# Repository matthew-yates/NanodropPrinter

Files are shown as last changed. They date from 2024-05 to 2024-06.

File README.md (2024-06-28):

# Nanodrop Printer

Syringe dispenser for accurately placing nanoliter scale liquid droplets on surfaces.

### XYZ motion hardware

The XYZ motion platform hardware is the [OpenBuilds C-Beam Machine](https://openbuildspartstore.com/openbuilds-c-beam-machine/):

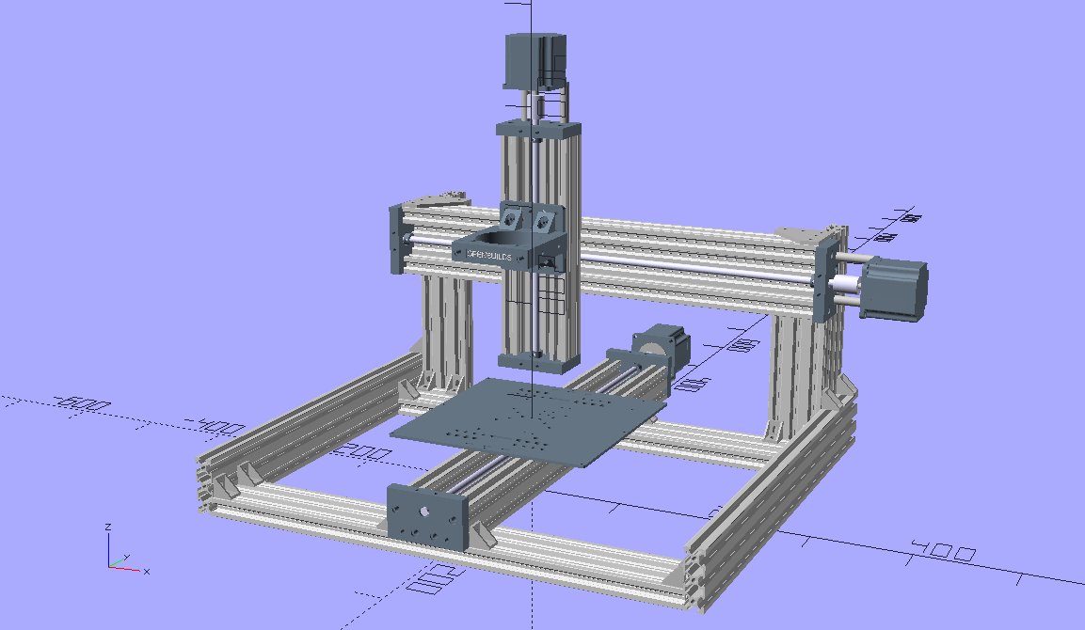
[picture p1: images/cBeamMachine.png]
C-Beam Machine


Identical [NEMA-23 stepper motors](https://openbuildspartstore.com/nema-23-stepper-motor/) with peak current of 2.8 A are used for the X, Y, and Z axes.

Motion is transmitted through [8 mm diameter lead screws](https://openbuildspartstore.com/8mm-metric-acme-lead-screw/) with 8 mm lead.

Moving parts are connected to the lead screws using [anti-backlash nuts](https://openbuildspartstore.com/anti-backlash-nut-block-for-8mm-metric-acme-lead-screw/).

Stepper motors have 200 full steps per revolution. The motors are operated with 1/16 microstepping, giving 2.5 microns of linear motion per microstep.

### Electronics

A [24 V Meanwell power supply](https://openbuildspartstore.com/24v-meanwell-power-supply-bundle/) is used to provide a maximum of 14.6 A current.

The [SKR mini E3 V3](https://github.com/bigtreetech/BIGTREETECH-SKR-mini-E3) is used for controlling stepper motors. The board uses [TMC2209 stepper drivers](https://www.analog.com/media/en/technical-documentation/data-sheets/TMC2209_datasheet_rev1.08.pdf) that are capable of driving motors up to 2.8 A.  This control board has four identical stepper drivers because it is designed for use in 3D printers.  Three of the stepper drivers are used to control X, Y, and Z motion.  The fourth is used to control a stepper motor on a syringe pump used for liquid deposition.

### Syringe pump

The syringe pump hardware is taken from a model [NE-300 pump](https://www.syringepump.com/NE-300.php). The syringe plunger motion is through a platform connected to a lead screw using an anti-backlash nut.  The lead screw has a lead of 1.27 mm per revolution. The lead screw is turned using a stepper motor connected with a belt and pulley system giving a motor:screw revolution ratio of 28:15.  The NE-300 stepper motor is a [high precision NEMA-17](https://www.moonsindustries.com/series/nema-17-high-precision-hybrid-stepper-motors-b020402) with 400 full steps per revolution.  Using 1/16 microstepping results in linear movement of the syringe plunger of 0.1 microns per microstep.

### Control software

[Marlin firmware](https://marlinfw.org/) is used for motion control. The motion commands are written in [G-code](https://en.wikipedia.org/wiki/G-code) format and sent to the microcontroller on the control board via serial communication with an attached computer.

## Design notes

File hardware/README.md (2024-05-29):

## Z-axis hardware

The Z-axis linear actuator of the Openbuilds C-beam machine has a spindle mount for attaching tools when used as a CNC machine.  This spindle mount is used to attached a syringe pump and BL-touch sensor.  The fully assembled Z-axis is illustrated below.

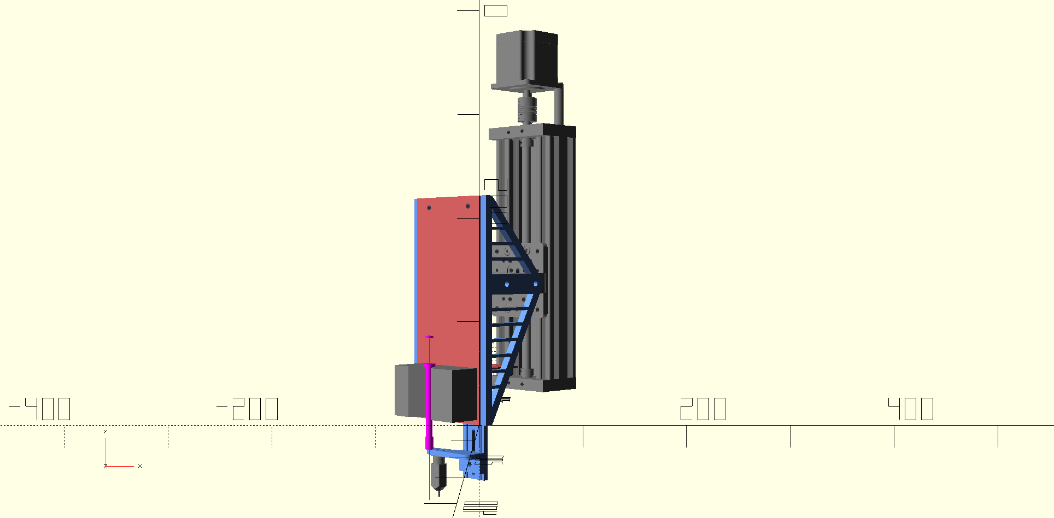
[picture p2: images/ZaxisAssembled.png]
Assembled BL-touch bracket


The image shows the approximate geometry of a mounted syringe and BL-touch sensor.  Folders in this hardware section of the repository include:

* [syringePump](https://github.com/matthew-yates/NanodropPrinter/tree/main/hardware/syringePump): Instructions with photographs for creating pump mounting plate from a model NE-300 syringe pump.
* [pumpBracket](https://github.com/matthew-yates/NanodropPrinter/tree/main/hardware/pumpBracket): Images, instructions, and OpenSCAD design files for 3D printed bracket for attaching syringe pump plate to spindle mount.
* [BLtouchMount](https://github.com/matthew-yates/NanodropPrinter/tree/main/hardware/BLtouchMount): Height adjustable mount for BL-touch sensor. Instructions and design files for 3D printing.

## Spring loaded plotter pen

In order to create fiducial markers for printing, the nanodroplet printer is used as a pen plotter. Fiducial markers are plotted on paper fixed to the glass platter printing surface. This approach ensures that the fiducial markers are aligned with the X and Y axes of the nanodroplet printer.

The widely available Pilot G2 Ultra Fine gel pen was selected for plotting. The refill cartridge was removed from the pen and used in a custom built holder that uses a spring to provide relatively constant force of the pen tip on paper. Design files and instructions for creating the spring loaded plotter pen are found in: [penPlotter](https://github.com/matthew-yates/NanodropPrinter/tree/main/hardware/penPlotter).

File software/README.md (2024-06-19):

# Instructions

## 1. Set up laptop for external instrument control

Although any operating system can be use in principle, all development and testing was done using the Debian Linux operating system.  The instructions here refer to that operating system and should be applicable to other Debian-based operating systems (Ubuntu, Mint, etc.).

### 1.1 Python related packages

After installing the Linux operating system, run the following command as root to install Python related packages:

```
apt install python3-full python3-numpy python3-scipy python3-sympy python3-matplotlib python3-opencv python3-pandas python3-serial python3-spyder jupyter-notebook
```

The above commands install a number of libraries used for scientific and numerical methods, serial communication, computer vision, the Spyder IDE for editing code, and Jupyter notebook client for running code interactively.

### 1.2 Serial communication

The user needs to be added to the "dialout" group in order to gain required permissions for sending commands to the printer. Run the following command as root to do this:

```
usermod -a -G dialout $USER
```

Where "$USER" is the name of the user to be added to the dialout group.

It is also recommended that PuTTY serial console be installed by running the following command as root:

```
apt install putty
```

PuTTY is not required, but can be useful in troubleshooting. To open a serial console to the instrument, use the speed (baudrate) setting of 115200.  The serial line is normally "/dev/ttyACM0". The serial line can be confirmed by running the command "dmesg" as root immediately after plugging the instrument into a USB port.  The PuTTY console can be left running in the background in order to display responses from the instrument.  For example, sending the G-code command "M119" will cause the instrument to respond with the current logic state of all endstop switches, which will be displayed on the PuTTY console.

### 1.3 PlatformIO

The [PlatformIO](https://docs.platformio.org/en/latest/core/index.html) command line interface is used for compiling the Marlin firmware. It is recommended that PlatformIO be installed on the laptop used for instrument control to facilitate making changes to firmware settings. First, install curl by running the following command as root:

```
apt install curl
```

Next, run the following two commands as a normal user:

```
curl -fsSL -o get-platformio.py https://raw.githubusercontent.com/platformio/platformio-core-installer/master/get-platformio.py
python3 get-platformio.py
```

This installation script will create a Python virtual environment in the user home directory in which platformio is installed.  The following two commands can be run as root to provide system-wide commands "platformio" and "pio" for any user to run:

```
ln -s /home/$USER/.platformio/penv/bin/platformio /usr/bin/platformio
ln -s /home/$USER/.platformio/penv/bin/pio /usr/bin/pio
```

Where "$USER" is the name of the user account used to run the platformio installation script.

## 2. Configure and install Marlin

A fork of the Marlin firmware used for the the SKR mini E3 V3.0 board is maintained in in a separate repository:

[https://github.com/matthew-yates/Marlin](https://github.com/matthew-yates/Marlin)

This repository can be downloaded as a zip archive.  After extracting the archive, run the following two commands as normal user from the directory containing the "platformio.ini" file:

```
platformio run --target clean -e STM32G0B1RE_btt_xfer
platformio run -e STM32G0B1RE_btt_xfer
```

The resulting compiled firmware will be found in the hidden subdirectory named ".pio/build/STM32G0B1RE_btt_xfer" found in the same directory that contains the "platformio.ini" file.

The compiled firmware is named "firmware.bin". Copy the compiled firmware to a microSD card formatted with the FAT32 filesystem. Insert the microSD card into the slot on the SKR mini E3 V3.0 board. The firmware will be installed from the microSD card automatically when the board is powered on.

The forked Marlin repository linked above contains the configuration files "Configuration.h" and "Configuration_adv.h" that can be edited if firmware changes are needed.

## 3. Motion calibration

### 3.1 X and Y axis lead screw calibration and XY plane skew

Refer to the README in the directory [leadCalibration](https://github.com/matthew-yates/NanodropPrinter/tree/main/software/leadCalibration). The calibration pattern provided is plotted using a pen plotter to calibrate linear travel per rotation of the lead screw and check for skew in the XY plane.

### 3.2 Z-axis syringe pump lead screw calibration

Movement on the Z-axis and syringe pump lead screws was measured using electronic calipers.  The microsteps per mm settings in the firmware were adjusted until the actual movement matched programmed movement.

### Camera calibration

A USB microscope is used to measure distances from images.  Accurate distances are needed for calculating XY coordinates for target printing locations.  Before the camera can be used for measurements, it must be calibrated by calculating the distance between two points on an image in pixels separated by a known distance in millimeters. A microscope calibration pattern is used for this purpose.

The Jupyter notebook file "cameraCalibration.ipynb" contains detailed annotated code for calibrating the camera. The following steps are involved:

1. The USB microscope is focused on the calibration pattern and an image of this pattern is saved using OpenCV. 
2. Two x,y pixel coordinates on the image then selected via mouse click. These points have a known distance in millimeters between them from the calibration pattern.
3. The distance between points in pixels is calculated.
4. Five repeated calibration measurements are taken, and the mean, maximum, minimum and standard deviation of the measured pixels per mm is reported.
5. The mean value is stored in a text file for future use as a conversion factor between pixels and millimeters.

The image below is an example image taken after clicking two calibration points.  In this case, a 5 mm calibration distance was selected and the microscope image was 1600x1200 pixels.

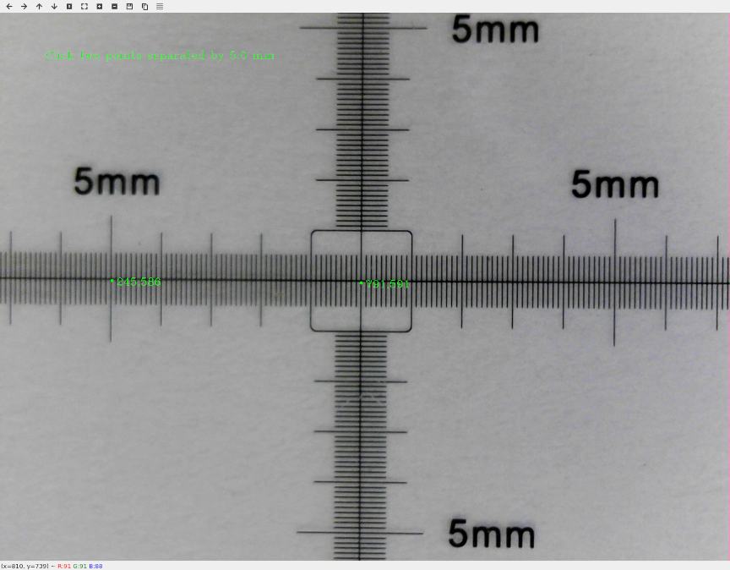
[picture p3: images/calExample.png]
example calibration image


### Fiducial marker

A fiducial marker is needed for alignment of the camera with the printer as well as accurately measuring locations of desired droplet deposition locations.  A variety of marker patterns are suitable for this purpose as long as there is a clear point that can be selected as the origin for x,y coordinates, as well as vertical and horizontal lines that define the directions of the printer axes.  An example marker is shown below.

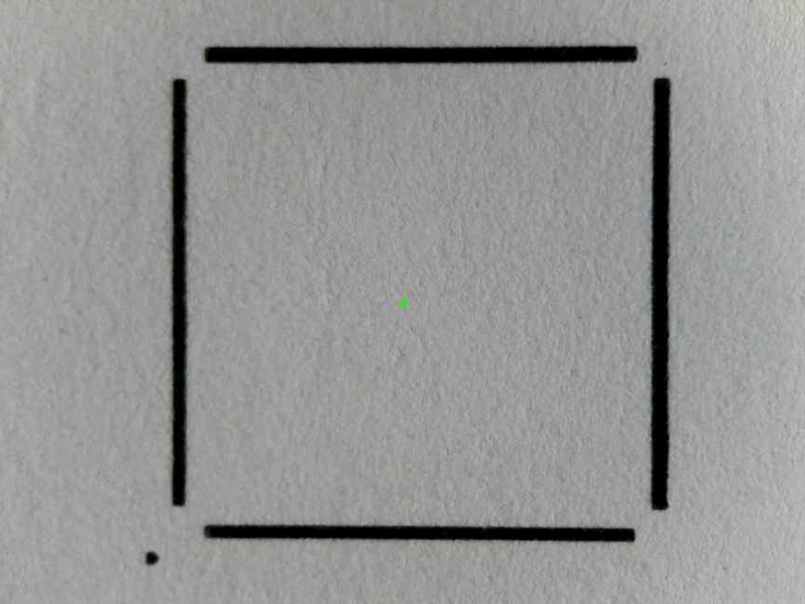
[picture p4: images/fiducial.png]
example fiducial marker


This marker has 4 lines, 8 mm x 0.2 mm each that are arranged to the edges of a 9 mm by 9 mm square shape.  The 9x9 mm^2 box defines an area in which small objects may be placed for selecting and measuring printing locations.  There is a small circle on the lower left that serves to mark the origin.  The above image is in scalable vector graphics format in the file "alignPattern.svg".

### Printer alignment with fiducial marker

The vertical and horizontal lines of the fiducial marker must be aligned with the y-axis and x-axis direntions of movement of the printer nozzle. The easiest way to achieve this is by using the printer itself as a plotter to create the fiducial marker. The syringe pump has a spring loaded clamp for holding a syringe. Instead of the syringe, clamp a fineliner marker or ultrafine technical pen.  Next, use the G-code file "alignMarker.gcode" to send motion commands needed to print the above pattern.  Before running the G-code commands, the marker should be placed in a starting position 1 mm above the target location of the origin dot. The print head is returned to this position after plotting the pattern.

### Camera alignment with the fiducial marker

Alignment of the camera image with the directions of the fiducial marker plotted by the printer is achieved by manually rotating the camera.  After it is aligned, the camera is clamped into position. To facilitate alignment, the Jupyter notebook "cameraAlignment.ipynb" can be used. The Python+OpenCV script places vertical and horizontal lines on the camera video feed. An example of camera alignment is shown in the image below.

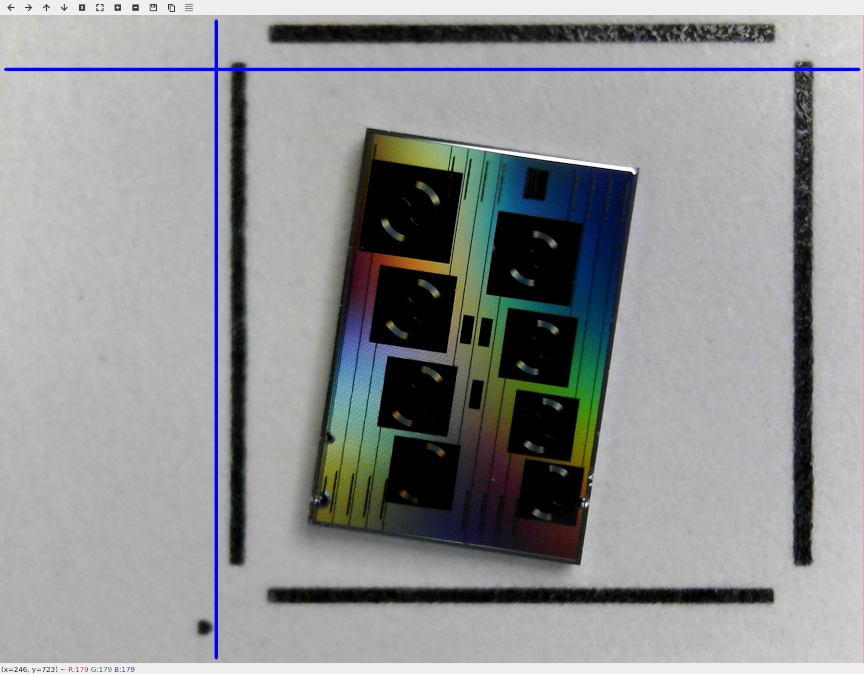
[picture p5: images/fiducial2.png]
example camera alignment


In this image, the blue lines are parallel to the fiducial marker lines. There is also a small silicon-based photonic chip in this image that is the target object for subsequent printing.

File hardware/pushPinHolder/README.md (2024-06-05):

## Push pin holder

A needle point push pin was used for testing accuracy of motion. When the tip of the pin is pressed into a plastic printing surface, it leaves a mark that can be used for measuring location in XY coordinates. For these motion accuracy tests, a simple holder was designed, as shown below.

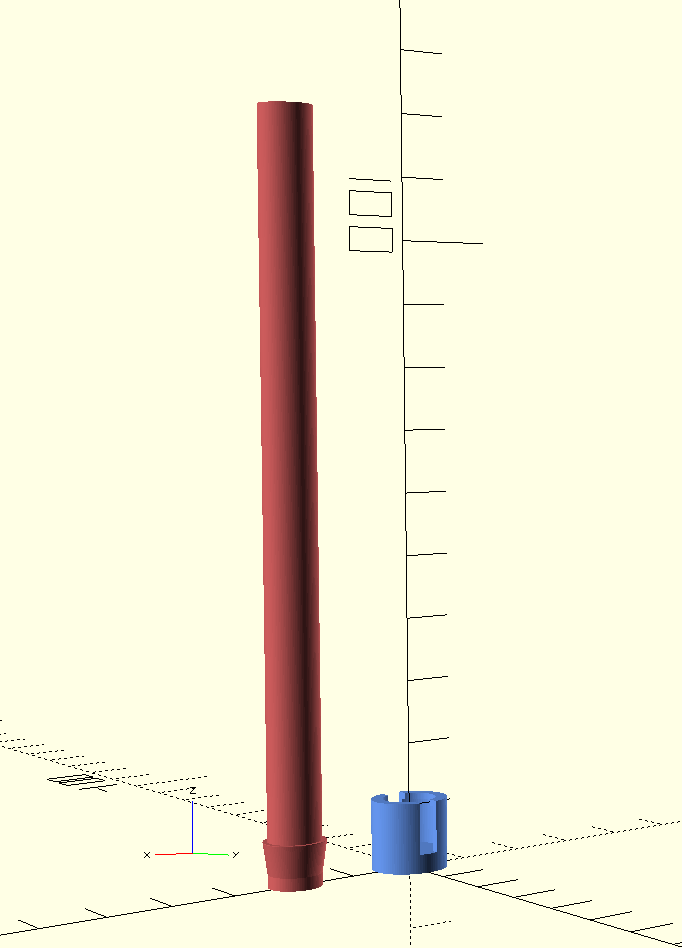
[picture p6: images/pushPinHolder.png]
push pin holder


It consists of a main body (shown in red) that has an annular ridge on the outside for attaching the cap (shown in blue). Before attaching the cap, the needle point pin is inserted through a small cylindrical opening. The fully assembled part is shown below with the needle illustrated in magenta.

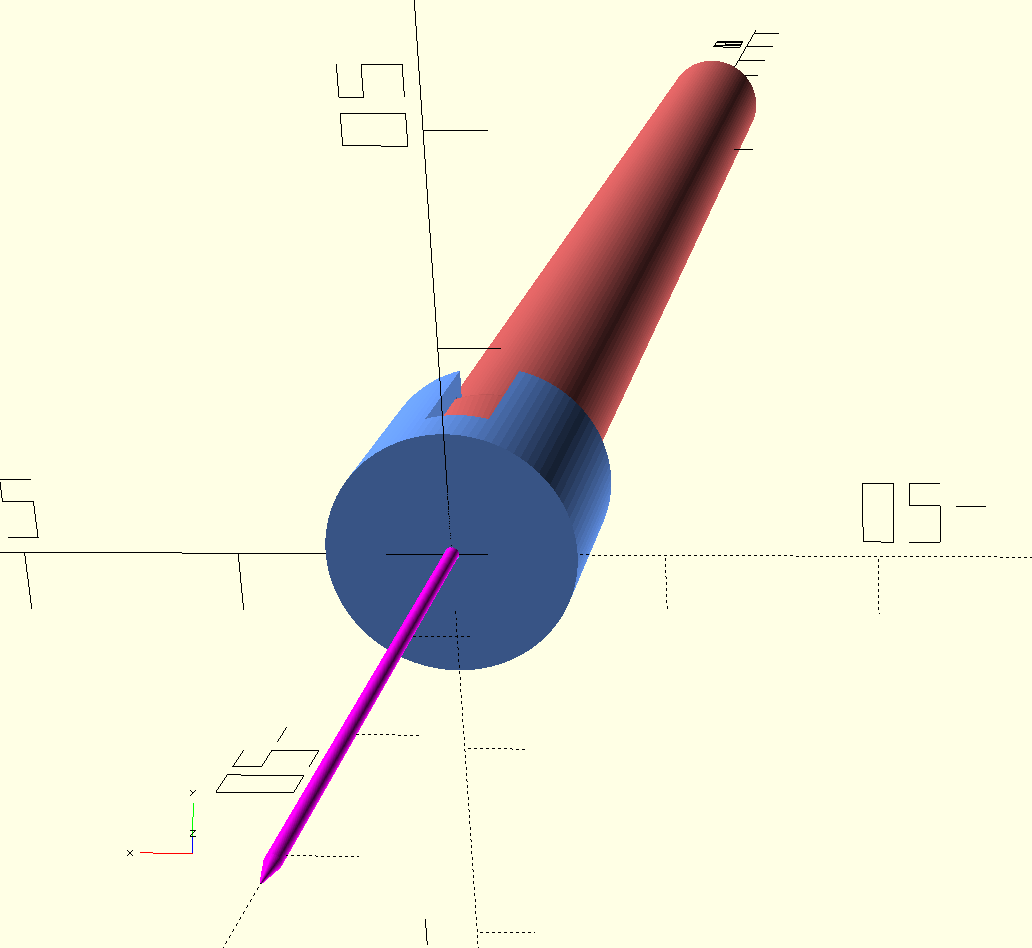
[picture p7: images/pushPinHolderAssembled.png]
assembled print bed with glass


The outer diameter of the main body of the holder is approximately the same as that of a Hamilton 25 microliter syringe model 80222. When the push pin holder is clamped into the syringe pump, the sharp point is therefore located at the approximately the same location as the center of a needle attached to the 25 microliter syringe.

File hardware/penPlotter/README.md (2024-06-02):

## Spring loaded pen

In order to ensure that fiducial markers are aligned with the X and Y axes of the nanodroplet printer, the printer itself was used as a pen plotter to draw lines. A variety of commercially available pens were tested for this purpose. The goal was to create very fine lines that are uniform in width. The widely available [Pilot G2 Ultra Fine](https://pilotpen.us/Product?0=40&1=29&cid=260) gel pen was selected. The manufacturer claims a line width of 380 microns. Testing showed the pen achieves relatively uniform line widths at or below 380 microns in width.  An example microscope image is show below of a hand drawn line on standard office copy paper. The microscope calibration ruler in the image measures in 100 micron increments. The image shows the pen produces a line ~300 microns in width. 

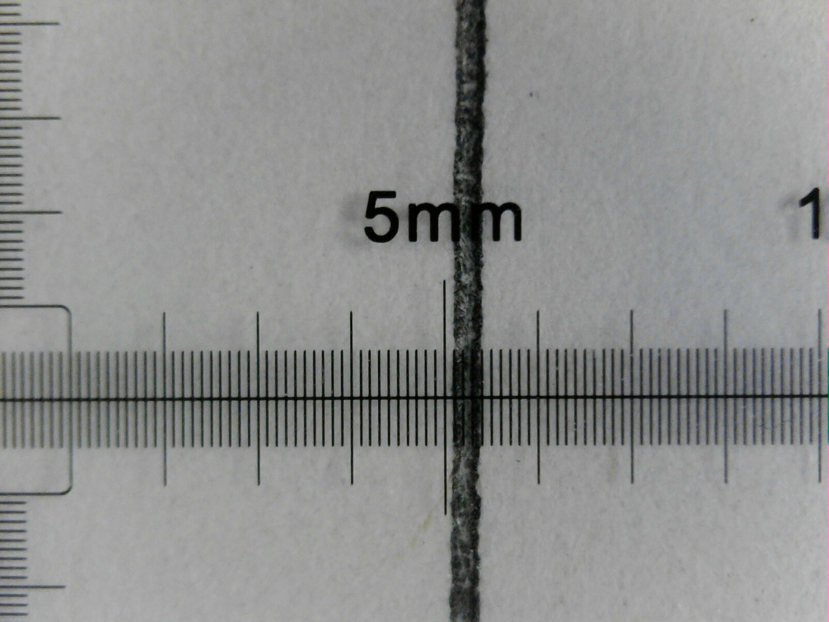
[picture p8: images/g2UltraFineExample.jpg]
pen line with microscope scale


The nanodroplet printer does not have an easy mechanism to control the force of contact of the pen in the Z-axis direction. To overcome this, a holder was developed that allows the pen tip a few millimeters of travel in the Z-axis direction. A spring is used to apply relatively constant force between the pen tip and plotting surface after contact is made.

### Fabrication and assembly

A 115.5 mm length piece is cut from [aluminum tubing](https://www.homedepot.com/p/Everbilt-36-in-x-1-2-in-x-1-16-in-Aluminum-Round-Tube-801247/204274002) having a nominal OD of 1/2 inch and wall thickness of 1/16 inch. A micrometer was used to measure the actual OD as 13 mm and ID as 9.7 mm. The aluminum tubing provides rigidity to minimize bending as the pen tip is dragged across the printing surface.

The Pilot G2 pen is disassembled to remove the refill and spring. The spring is re-used in the fabricated holder. The dimensions of the refill were measured by micrometer. A 3D model of the refill is provided in the file "ultraFineGelPen.scad".

Two parts must be 3D printed using the design file "ultraFineHolder.scad". The dimensions of these parts was determined by trial and error in order to have very right tolerances when printed using PETG filament. The library file "threadsDK.scad" created by Dan Kirshner is used for modeling threads for screwing the two parts together. The image of the 3D modeled parts is shown below.

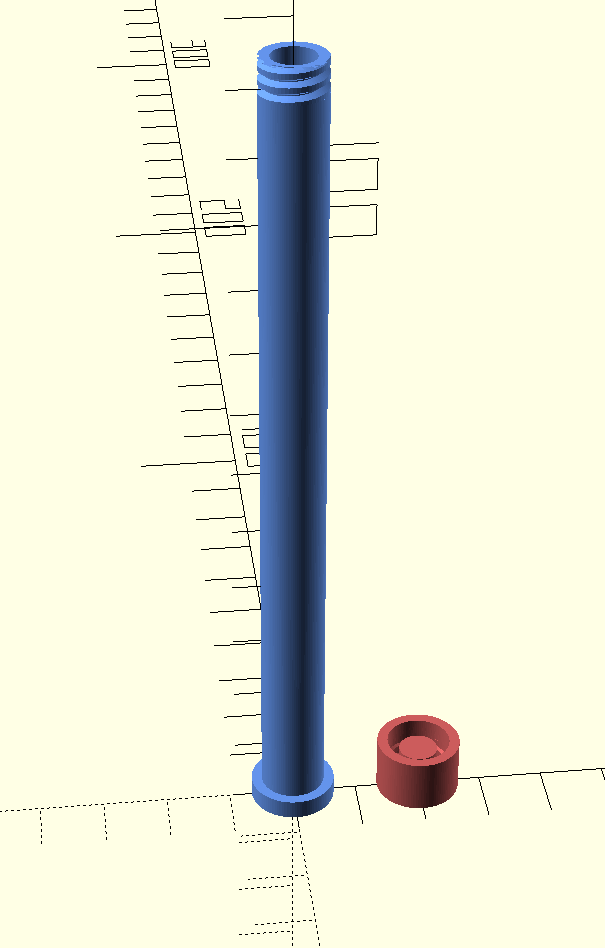
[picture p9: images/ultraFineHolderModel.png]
model used for 3D printed parts


After printing these parts, the long part shown in blue is slid inside the 115.5 mm long aluminum tube. The gel pen refill is inserted so that the pen tip extends out the hole at the base. The spring is inserted after the pen refill. The smaller part shown in red is screwed onto the top to compress the spring. An image of the final assembled part is shown below.

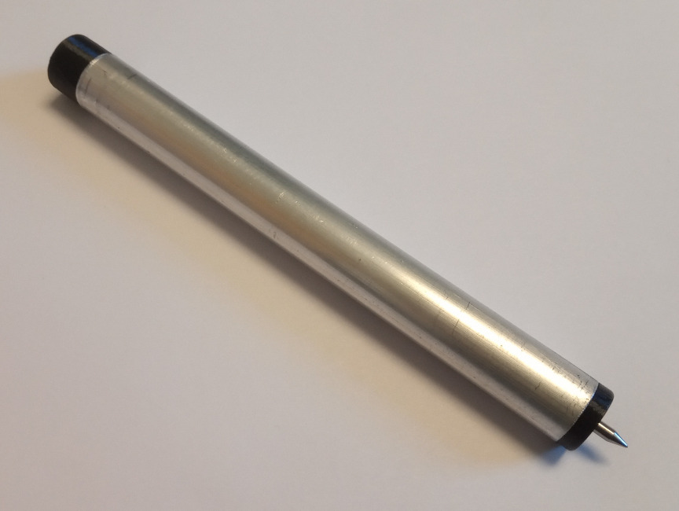
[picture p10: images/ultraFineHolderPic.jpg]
assembled spring loaded plotter pen

 
The plotter pen is attached to the syringe pump using the spring loaded clip normally used for syringes. A metal C-clamp is then used to firmly hold the plotter pen is place as it is dragged laterally across the printing surface during plotting. An adapter part was designed in "penClampClip.sscad", a model of which is shown below.

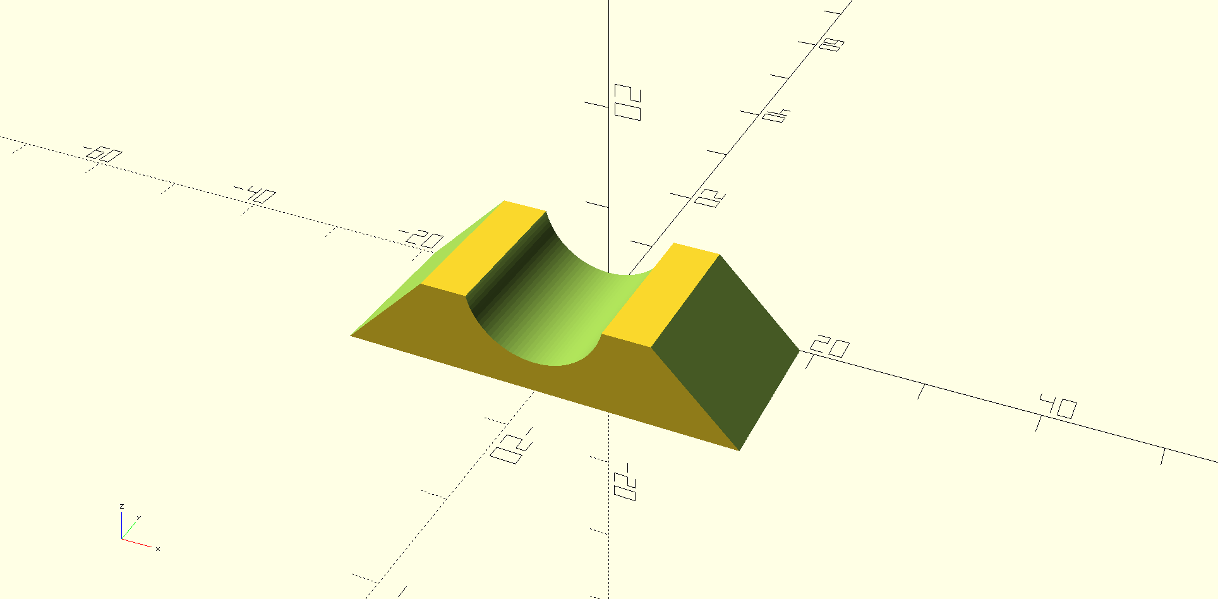
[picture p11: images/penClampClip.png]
plotter pen c-clamp adapter


This C-clamp adapter is placed on top of the plotter pen to prove a flat surface for attaching the clamp. An image of the fully assembled device with the plotter pen held by a small C-clamp is shown below.

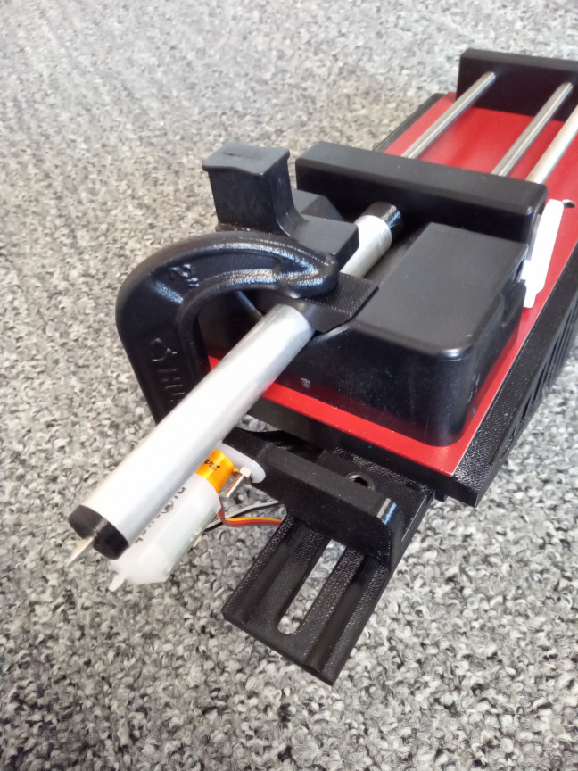
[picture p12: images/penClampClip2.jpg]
fully assembled plotter pen


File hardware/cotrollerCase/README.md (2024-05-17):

## Case for motion controller

Currently using the BigTreeTech SKR mini E3 V3.0 board with Marlin firmware to control movement.  The case for this control board and an LCD screen is decribed in a separate repository:

[https://github.com/matthew-yates/BTTskrE3v3_case](https://github.com/matthew-yates/BTTskrE3v3_case)

Possibly switching to a different control board in the future, which will require designing a new case.

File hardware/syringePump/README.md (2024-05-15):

## Syringe pump

The hardware for liquid dispensing is taken from a model [NE-330](https://www.syringepump.com/NE-300.php) syringe pump, illustrated below.

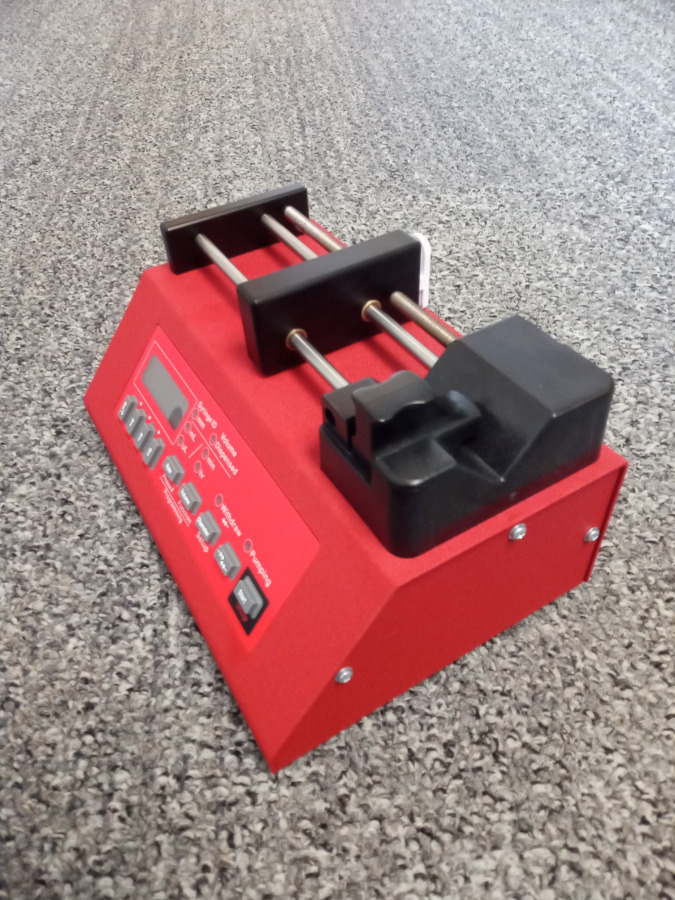
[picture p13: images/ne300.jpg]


The the pump is first fully disassembled. After removing all of the parts mounted to the top cover, it is cut along the approximate lines illustrated in green in the image below.

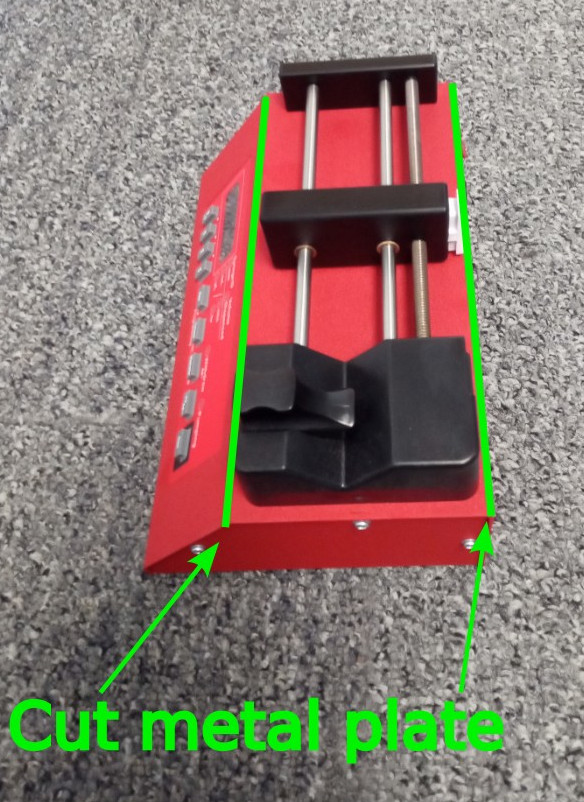
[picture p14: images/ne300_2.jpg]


The portion of the top cover cut out is a rectangle having dimensions of 92 mm by 222 mm. After cutting off the two screw tabs, the bottom side is flat.  An image of the cut out portion is shown below.  

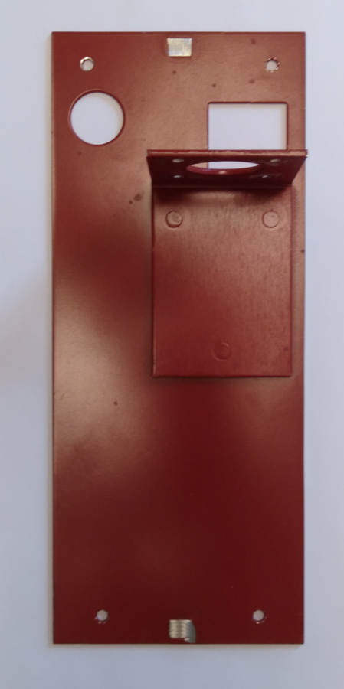
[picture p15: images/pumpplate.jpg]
pump plate image


The two screw tabs used to attach the top cover to the bottom cover were cut off.  This plate has a NEMA-17 stepper motor mount, large rectangular opening for the stepper belt/pulley connection between the stepper motor and the lead screw, and a large circular opening for the spring loaded syringe holder.  In addition, there are five small screw holes in the plate from the manufacturer.  These screw holes are used to attach parts to the plate using #6 coarse grain machine screws.  The NEMA-17 stepper is mounted to the motor mount using four M3 screws.

Not shown on the above image of the plate are two additional screw holes required for attaching the plate to the spindle mount on the XYZ positioning system.  These holes must allow M5 screws to pass through (~5.5 mm in diameter).  They are locate 9.2 mm from each long edge of the rectangle.  A 3D model of the plate was created in OpenSCAD that has precise dimensions of this plate.  The OpenSCAD code in this repository has the precise locations of all screw holes.  A rendering of this model is shown below.

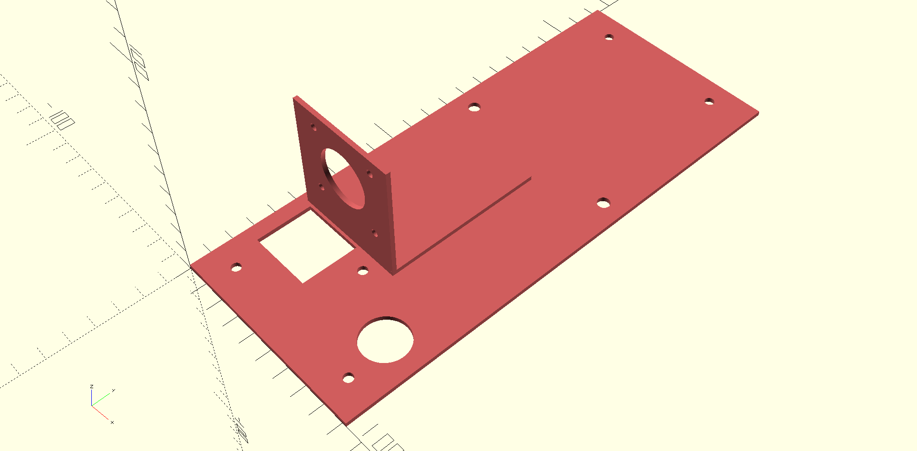
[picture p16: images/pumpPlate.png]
pump plate 3D model


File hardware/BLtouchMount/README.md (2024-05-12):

## Adjustable BL-touch mounting bracket

This is a height adjustable mount for a [BL-Touch sensor](https://www.antclabs.com/bltouch).  The sensor allows the location of the printing surface to be detected.  This mounting bracket is placed on the back side of the syringe pump.  The adjustable height of the bracket allows it to be used with syringes of varying length.  The image below shows the two parts of the bracket colored in blue and red.

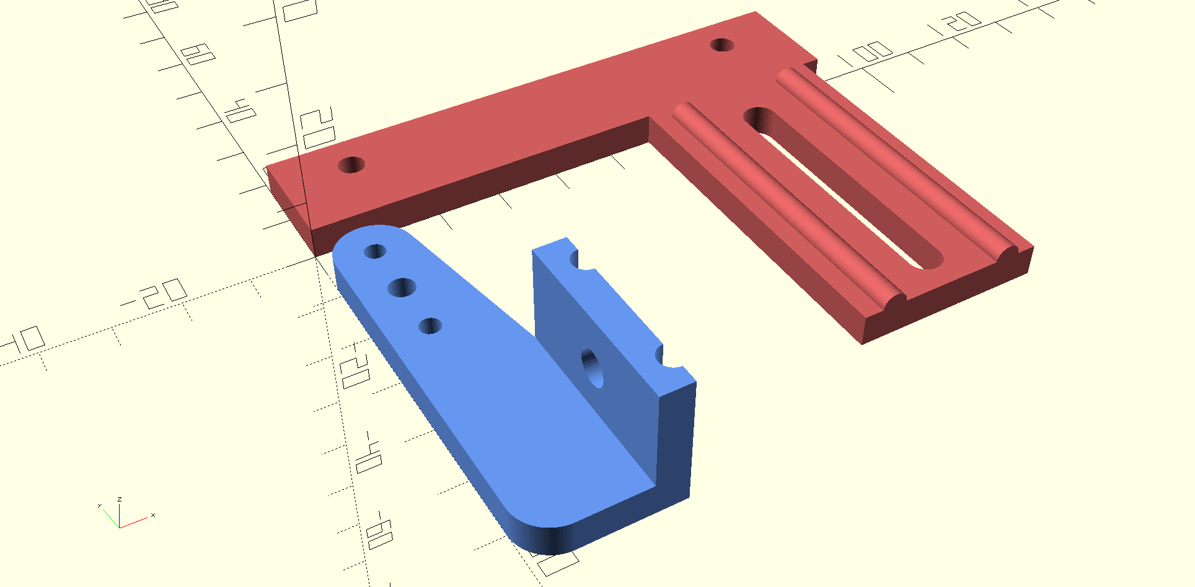
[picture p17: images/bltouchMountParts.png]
Bracket to mount BL-touch sensor


The next image below shows the two part bracket assembled with the BL-Touch sensor illustrated in gray.  The vertical slot in the bracket allows for height adjustment using an M5 size screw and nut.

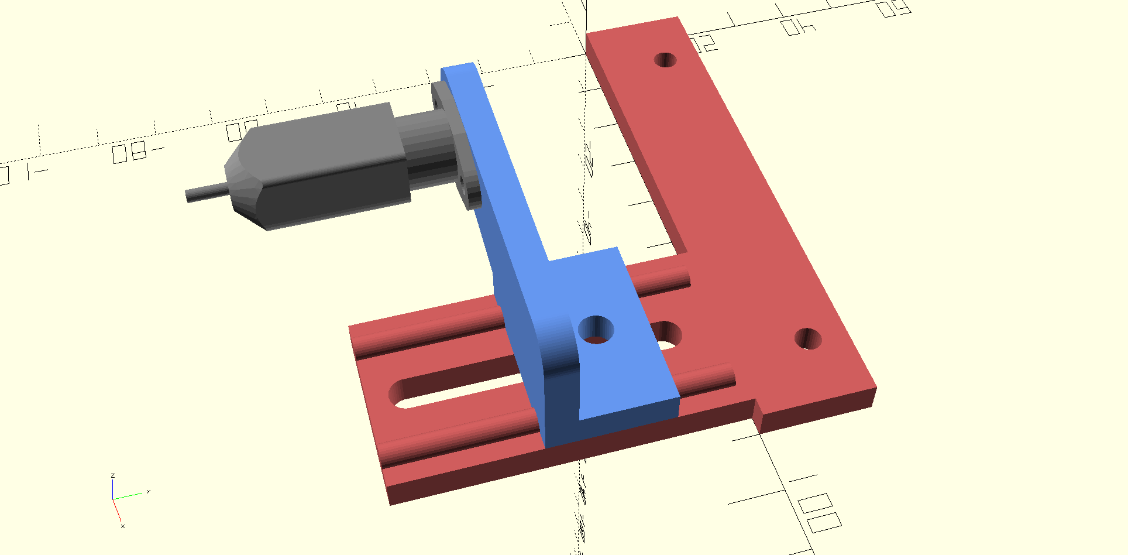
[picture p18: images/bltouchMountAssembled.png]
Assembled BL-touch bracket


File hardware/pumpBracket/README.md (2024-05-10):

## Syringe pump mounting bracket

The NE-300 syringe pump hardware is mounted to the spindle mount on the Openbuilds C-beam machine. The image below shows the rendering of the mounting bracket in blue.  The part of the spindle mount is shown in gray. The syringe pump parts are shown in red.  The bracket is secured to the spindle mount using M5 screws on the existing tapped holes. 

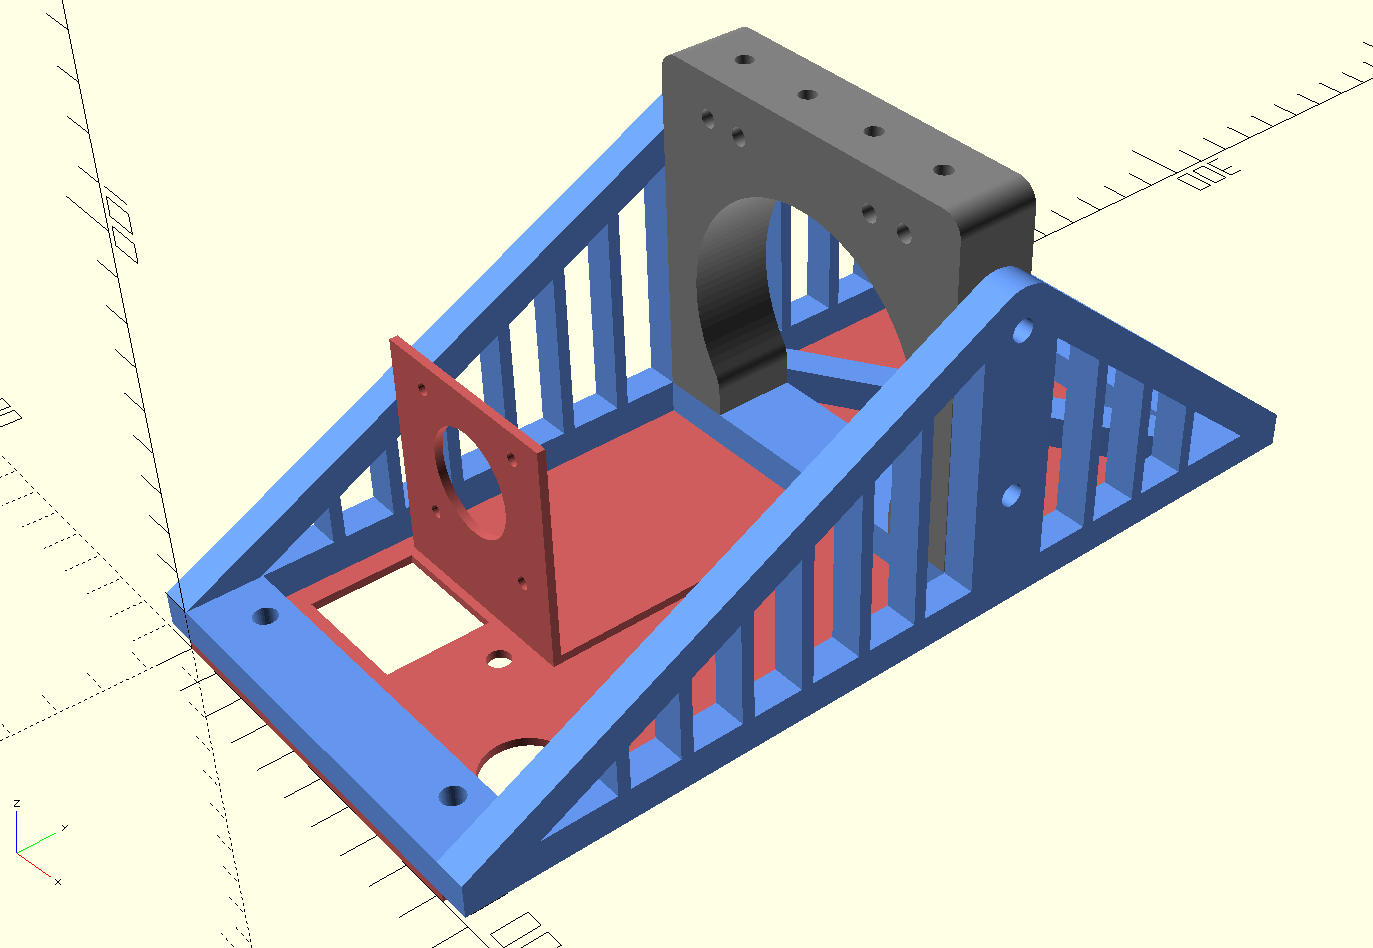
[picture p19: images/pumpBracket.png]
Bracket to mount syringe pump


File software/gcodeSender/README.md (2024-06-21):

## Sending G-code motion commands via serial communication

The Jupyter notebook "gcodeSender.ipynb" is used to send an arbitrary sequence of G-code motion commands from an attached laptop through USB serial connection to the printer.  The motion commands are read from a comma separated variable file that has absolute positions of X, Y, Z, and E (syringe pump/extruder) in individual columns.  Two example csv files are provided that can be used with a pen plotter.  The file "circle.csv" plots a single circle having a radius of 30 mm.  The file "plotPoints.csv" produces 4 concentric rectangles used for linear lead screw travel calibration.

When sending commands via serial communication, the commands must be spaced apart in time in order to avoid overflowing the buffer on the printer controller.  When serial commands are sent too quickly, the buffer overflow will cause commands to be skipped. The Python script calculates the time required for each movement based on the maximum travel speed settings in firmware which are 5 mm/s for X, Y, and Z axes and 0.7 mm/s for the E axis (syringe pump plunger). Sleep times are added between motion commands to allow enough time for printer movement to complete before issuing the next motion command.

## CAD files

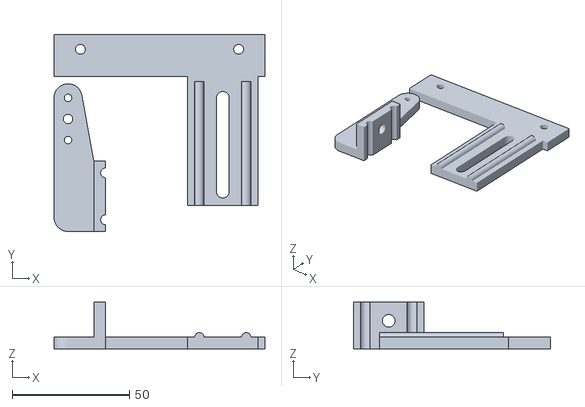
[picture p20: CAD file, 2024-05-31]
hardware/BLtouchMount/bltouchMountParts.stl
90.0 x 84.0 x 20.0

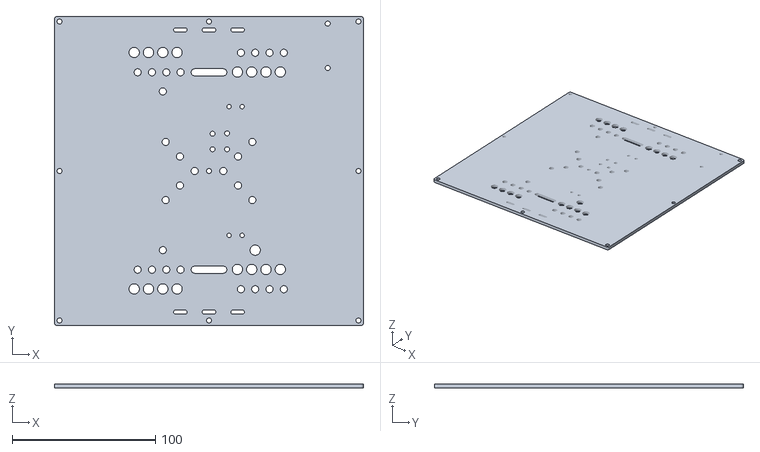
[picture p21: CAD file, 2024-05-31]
hardware/printBed/buildPlate.stl
216.0 x 216.0 x 3.00

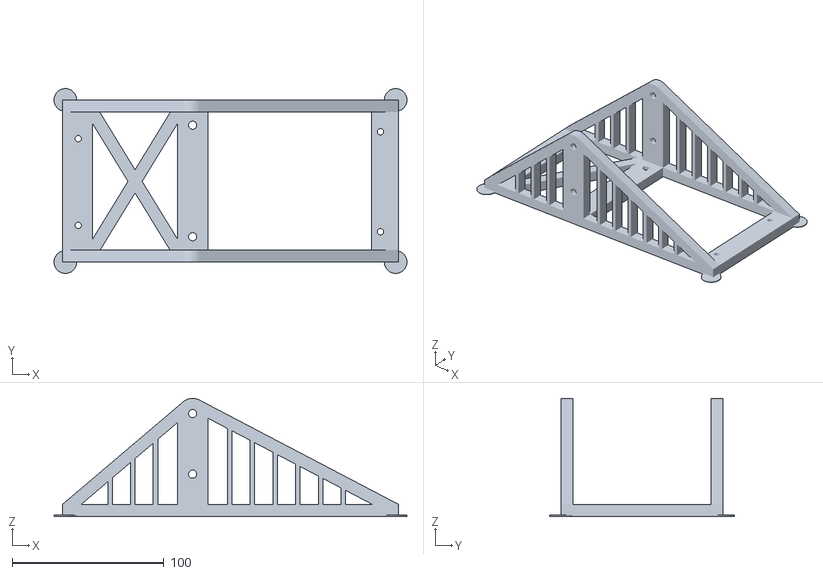
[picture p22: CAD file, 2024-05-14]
hardware/pumpBracket/pumpBracket.stl
233.0 x 122.0 x 78.0

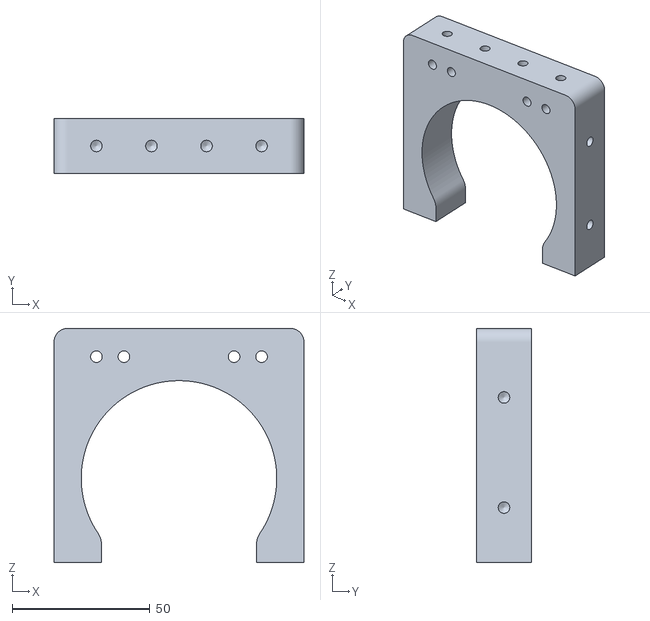
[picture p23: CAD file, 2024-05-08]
hardware/pumpBracket/spindlemount.stl
90.8 x 20.0 x 85.1

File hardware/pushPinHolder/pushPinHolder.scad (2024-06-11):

$fa = 1;
$fs = 0.4;
$fn=100;

color("cornflowerblue"){
difference(){
    cylinder(h=11.2,r=5.9);
    translate([0,0,3]) cylinder(h=11,r=4.9);
    translate([-1.5,-7.5,3]) cube([3,15,12]);
    translate([0,0,-1]) cylinder(h=5,r=0.5);
    translate([0,0,2]) cylinder(h=3,r=1.);
    }
difference(){
    translate([0,0,10.2]) cylinder(h=1,r=5.9);
    translate([0,0,3]) cylinder(h=11,r=4.2);
    translate([-1.5,-7.5,3]) cube([3,15,12]);
    }
}
        
translate([20,0,0])
color("indianred"){
difference(){
    union(){
        hull(){
            translate([0,0,2]) cylinder(h=0.1,r=4.1);
            translate([0,0,7]) cylinder(h=0.1,r=4.8);
            }
        cylinder(h=120,r=4.1);
        }
    translate([0,0,5]) cylinder(h=119,r=3.25);
    }
}

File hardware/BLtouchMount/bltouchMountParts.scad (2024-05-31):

$fa = 1.0;
$fs = 0.4;
translate([11,-60,5]) rotate([0,180,0])
// Vertical adjustment mount
color("cornflowerblue"){
    // bottom plate
    difference(){
        hull(){
            translate([5,0,0]) cylinder(h=5,r=6);
            translate([5,51,0]) cylinder(h=5,r=6);
            translate([-6,-6,0]) cube([5,30,5]);}
        // screw holes for top of BL touch
        translate([5,33,-1]) cylinder(h=7,r=1.6);
        translate([5,51,-1]) cylinder(h=7,r=1.6);
        // center hole on BL touch
        translate([5,42,-1]) cylinder(h=7,r=2);
        // slots for vertical adjustment
        translate([-11,-1,-1]) cylinder(h=27, r=2.1);
        translate([-11,19,-1]) cylinder(h=27, r=2.1);}
    // side plate
    difference(){
        translate([-11,-6,-15]) cube([5,30,20]);
        // M5 screw hole for height adjustment
        translate([-15,9,-7]) rotate([0,90,0]) cylinder(h=10,r=2.7);
        // slots for vertical adjustment
        translate([-11,-1,-16]) cylinder(h=27, r=2.1);
        translate([-11,19,-16]) cylinder(h=27, r=2.1);
}}
//Bracket to attach to pump
color("indianred"){
difference(){
    union(){
        cube([90,18,5]);
        translate([57,-55,0]) cube([30,55,5]);
        translate([62,-55,5]) rotate([-90,0,0]) cylinder(h=53,r=2);
        translate([82,-55,5]) rotate([-90,0,0]) cylinder(h=53,r=2);}
    // slot for vertical adjustment
    hull(){
    translate([72,-49,-1]) cylinder(h=7,r=2.7);
    translate([72,-9,-1]) cylinder(h=7,r=2.7);}
    // #6 screw holes for mounting
    translate([11.25,11.7,-1]) cylinder(h=7,r=2.1);
    translate([78.75,11.7,-1]) cylinder(h=7,r=2.1);}}

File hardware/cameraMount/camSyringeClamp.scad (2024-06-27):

$fa = 1.0;
$fs = 0.4;
// Using 25 ul syringe: maine body in clamp radius = 3.85 mm
// camera body radius = 6 mm
translate([0,16,0]) rotate([90,0,0])
difference(){
    translate([-25,0,8.]) cube([50,30,8]);
    translate([0,-1,5.445]) rotate([270,0,0]) cylinder(r=3.85, h=32);
    translate([0,-1,20.445]) rotate([270,0,0]) cylinder(r=6, h=32);
    rotate([0,45,0]) translate([0,-1,0]) cube([47,47,34]);
    rotate([0,-45,0]) translate([-47,-1,0]) cube([47,47,34]);
}

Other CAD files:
hardware/cameraMount/threadsDK.scad
hardware/cameraMount/tripodScrew.scad
hardware/penPlotter/penClampClip.scad
hardware/penPlotter/threadsDK.scad
hardware/penPlotter/ultraFineGelPen.scad
hardware/penPlotter/ultraFineHolder.scad
hardware/printBed/buildPlate.scad
hardware/printBed/printBedParts.scad
hardware/pumpBracket/pumpBracket.scad
hardware/syringePump/pumpPlate.scad

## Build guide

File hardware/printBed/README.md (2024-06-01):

## Print bed

The OpenBuilds C-beam machine uses a [build plate](https://openbuildspartstore.com/build-plate/) as the motion platform. This build plate has a number of different sized holes and slots for mounting various accessories to it. A parametric model of the build plate was created and is provided in OpenSCAD format ("buildPlate.scad"). Some of the holes in the build plate are used for attaching motion transmission hardware in the C-beam machine, but the M3 sized screw holes along the left and right side of the plate are available for mounting a print bed.

For the print bed, the primary qualities required are planarity and stiffness so that the . A glass plate (235x235x4 mm) was chosen as the print bed. This glass plate is a standard size used by several manufacturers of 3D filament printers. Glass plates of this size may be found from a variety of retailers as a 3D printer plate. Glass is advan

In order to attach the 235x235 mm glass print bed to the 216x216 mm build plate, custom clamps were designed and 3D printed. The image below illustrates the assembled print bed without the glass plate. The build plate is shown in gray. 3D printed supports for the corners of the glass are shown in blue. These supports are attached to the build plate with M3 screws. Corner clamps are shown in red. The corner clamps are held in place with M5 screws in slots that provide a slight adjustment to allow easy removal and replacement of the glass plate.

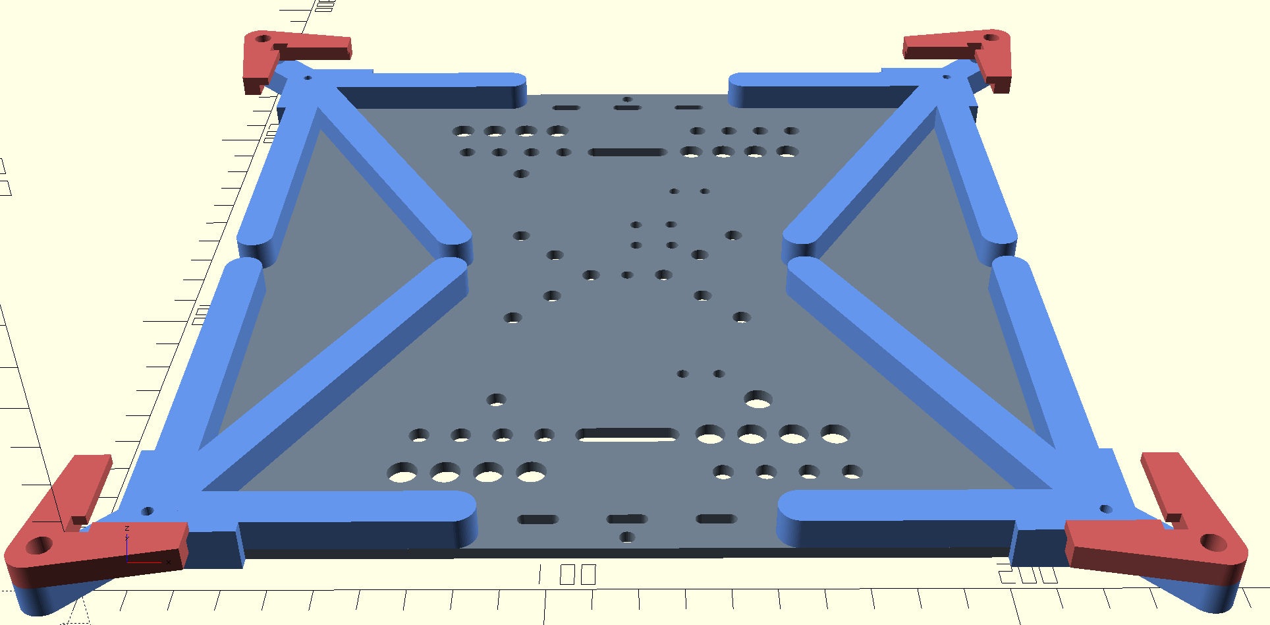
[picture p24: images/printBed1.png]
assembled print bed without glass


The second image below is the fully assembled print bed with the 235x235x4 mm glass plate illustrated in white.

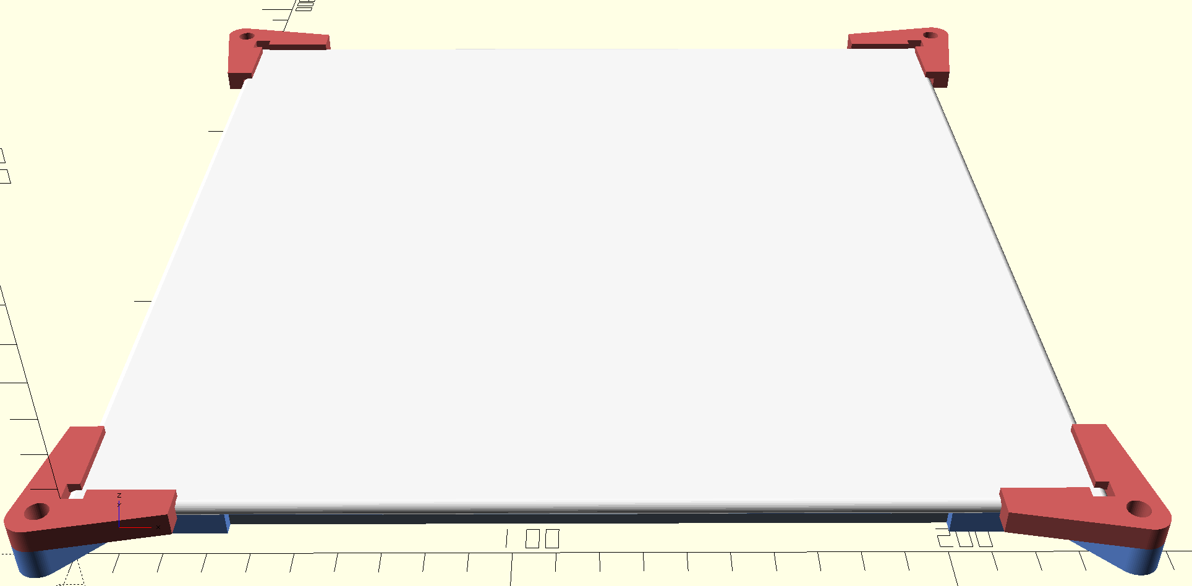
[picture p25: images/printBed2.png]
assembled print bed with glass


The parametric design file for the 3D printed parts is provided in "printBedParts.scad". In this file, half the required parts (two corner clamps, one left side support, and one right side support) are arranged for a single print job, as illustrated below.  The print job must be run twice to produce all of the required parts.

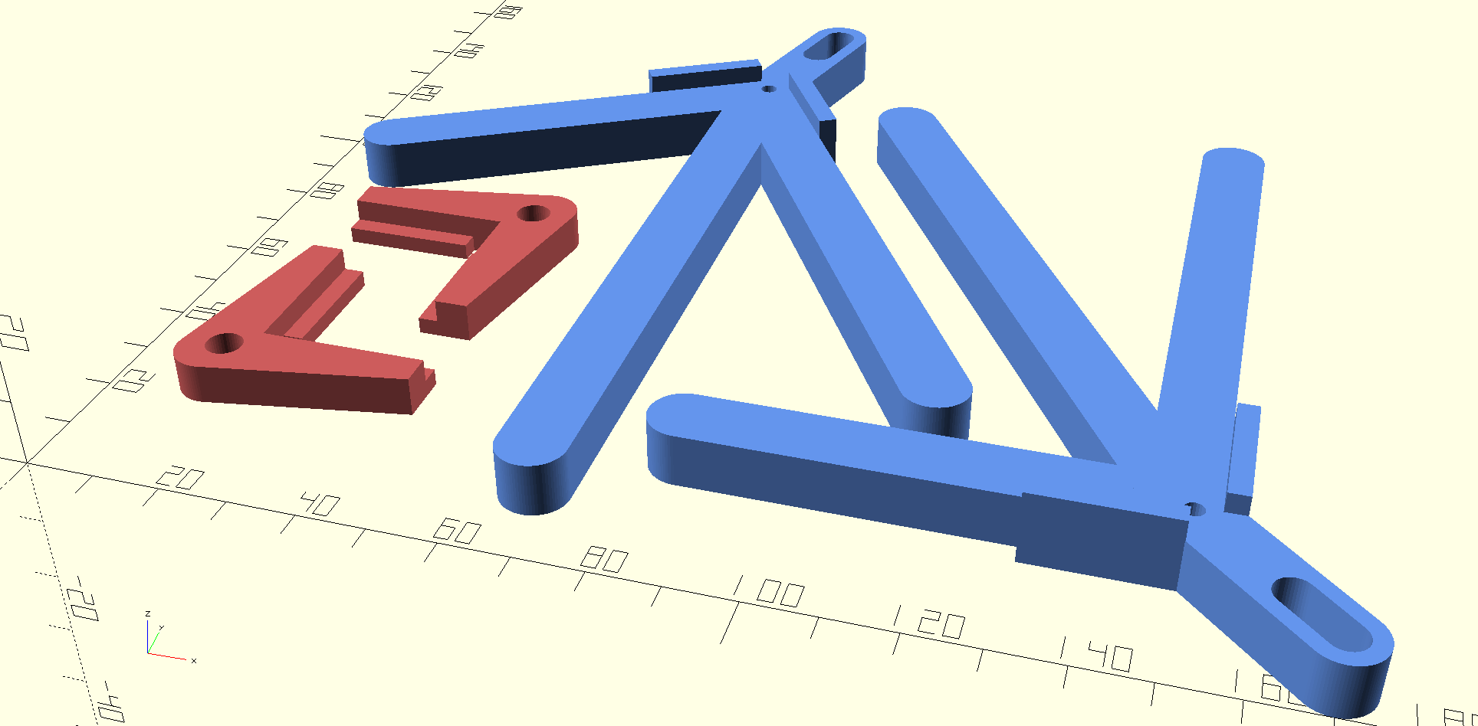
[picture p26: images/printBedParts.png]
print bed parts


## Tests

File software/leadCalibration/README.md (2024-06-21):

## X and Y axis lead screw calibration and skew correction for XY plane

The lead screws provided by the Openbuilds C-beam machine nominally provide 8 mm of linear travel for each rotation of the screw.  However, testing revealed that these screws consistently provide slightly more linear travel per revolution than the manufacturer specifies. If 8 mm of linear travel is assumed, the firmware should be configured to for 800 stepper motor microsteps per mm linear travel when using 1/32 microstepping. The [spring loaded plotter pen](https://github.com/matthew-yates/NanodropPrinter/tree/main/hardware/penPlotter) was used to draw calibration patterns on paper in order to measure the actual linear distance traveled using a setting of 800 microsteps per mm. The microsteps per mm firmware settings were then adjusted to correct for the lead screw inaccuracy on the X and Y axes.

Tape a sheet of paper 8.5x8.5 inches (216x216 mm) to the center of the glass print bed. Home the Z-axis and ensure that the tip of the pen contacts the paper when Z is at a height of zero.

Using the [G-code sender](https://github.com/matthew-yates/NanodropPrinter/tree/main/software/gcodeSender) with the data file "plotPoints.csv" will plot four concentric squares having sides 170, 120, 70, and 20 mm in length, respectively.  The sides of the squares are parallel to the X and Y axes of the printer.  After plotting, the length of each side of the squares printed on paper was measured.  The microsteps per revolution settings for X and Y axes were then adjusted until the lengths printed on paper match those expected from the calibration pattern design. It was found that the lead screws actually provide ~8.08 mm of linear travel per revolution. This ~1% difference from manufacturer specifications was corrected by proportionately reducing the microsteps per revolution settings in the firmware.

The square calibration patterns were also used to check for skew in the XY plane. If the X and Y axes of the printer are not exactly exactly perpendicular, the plotted pattern will be a parallelogram. To check for skew, the diagonal length connecting corners of the squares was measured and compared to that expected for 90 degree angles at the corners. Marlin firmware has an option to correct for skew, but it was found that this was not needed since care was taken during machine assembly to ensure X and Y axes were perpendicular.

## Z axis and syringe pump lead screw calibration

For these two lead screws, motion was measured using electronic calipers. The steps per mm settings in firmware were adjusted until actual motion matched programmed motion.

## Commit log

2024-05-08 Add files via upload
    design files for 3D printed bracket to mount syringe pump to spindle mount
    [pumpBracket.scad]
2024-05-08 Add files via upload
    pump bracket with spindle mount
2024-05-08 Add files via upload
    created from OpenBuilds STEP model on GrabCAD
    [spindlemount.stl]
2024-05-08 Add files via upload
    created from scad code
    [pumpBracket.stl]
2024-05-09 Add files via upload
    new bracket design
2024-05-10 Update pumpBracket.scad
    fixed typo
    [pumpBracket.scad]
2024-05-10 Add files via upload
    new design to facilitate printing
2024-05-10 Add files via upload
    fixed hole sizes and made design changes to facilitate printing
    [pumpBracket.scad]
2024-05-11 Add files via upload
    height adjustable BL touch mount
    [bltouchMountParts.scad]
2024-05-11 Add files via upload
    for printing both parts
    [bltouchMountParts.stl]
2024-05-13 Add files via upload
    corrected hole size and location
    [bltouchMountParts.scad]
2024-05-13 Add files via upload
    corrected screw hole sizes and locations
    [pumpBracket.scad]
2024-05-13 Add files via upload
    corrected hole sizes and positions
    [pumpBracket.stl]
2024-05-14 Add files via upload
    changes to facilitate printing
    [pumpBracket.scad]
2024-05-15 Add files via upload
    ne-300 pump photo
2024-05-15 Add files via upload
    3D model of pump plate
    [pumpPlate.scad]
2024-05-15 Add files via upload
    actually #6 size screws, not #8
    [pumpBracket.scad]
2024-05-17 Add files via upload
    sensor now centered in line with syringe needle
    [bltouchMountParts.scad]
2024-05-17 Add files via upload
    Minor error in design code
    [bltouchMountParts.scad]
2024-05-17 Add files via upload
    fixed minor error in design dimensions
    [bltouchMountParts.stl]
2024-05-17 Add files via upload
    fixed hole and plate size
    [bltouchMountParts.scad]
2024-05-17 Add files via upload
    minor design change
    [bltouchMountParts.scad]
